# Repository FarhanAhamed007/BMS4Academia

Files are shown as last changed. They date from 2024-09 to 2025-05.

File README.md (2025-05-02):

# BMS4Academia



An educational Battery Management System (BMS) for academia: designed for students, research scholars, and hobbyist engaged in battery algorithm studies, enabling real-time testing of their algorithms and logics.

### Motive – To support research community with a habitat for testing of battery algorithms on battery packs

#### Developed for coherence and scalability 

### Key Features
-> Simple and community friendly Controller (ESP32S3)    
-> Master-Slave Architecture     
-> SPI and iso-SPI          
-> 3s to 100s configuration          
-> Cell balancing      
-> Contactor Control (12V/24V upto 3A) & Feedback      
-> CAN, RS485 and I2C Interface



I thank Rahul Marriesh for his contribution to 18s slave BMS development. 

I express my gratitude to Dr. Kaushal Jha, CEO of my center and co-guide, my guide Prof. Shankar Ram, and my mentor Dr. Sushant Mutagekar for their continuous support. I also extend my thanks to the **Center for Excellence in Energy and Telecommunication (CEET)** for providing the opportunity to develop this work. I am grateful to my ~~team~~ fam for their invaluable assistance and support throughout this project.

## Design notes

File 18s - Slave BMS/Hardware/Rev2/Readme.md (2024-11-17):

# 18s - Slave BMS      
## Design Language    
-> Simple design (2-Layer board)       
-> Easy to use       
-> Small in size (94mm x 90mm)

## Features     
-> Analog Devices AFE: LTC6813            
-> 0 - 5V voltage measurement of cells (NMC, LFP, LTO, Na-ion)        
-> Cell balancing up to 150mA per cell (External balancing)(balancing current can be increased by changing balancing resistors)       
-> SPI or Iso-SPI configurable          
-> Direct interface with any microcontroller (via SPI upto 18s)        
-> Configurable for temperature measurement via 10K thermistor or ADC for current measurement.     
-> 9x temperature sensing (thermistor based)         
                      (or)              
-> 8x temperature sensing (thermistor based) & 1x current sensing (AUX)       
-> Short circuit protection and wake-up interrupt by hardware design 

## PCB isometric


## PCB Sections & Connectors




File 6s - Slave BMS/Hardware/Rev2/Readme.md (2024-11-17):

# 6s - Slave BMS      
## Design Language   
-> Scalable (3 to 100s)      
-> Simple design (2-Layer board)           
-> dedicated current sensing port      
-> Small in size (51mm x 76mm)

## Features     
-> Analog Devices AFE: LTC6810         
-> 0 - 5V voltage measurement of cells (NMC, LFP, LTO, Na-ion, Zn-air etc...)        
-> Cell balancing up to 150mA per cell (internal balancing)       
-> SPI or Iso-SPI configurable          
-> External Power connector (Powering IC from external source instead of battery, useful for cells with low voltages like Zn-air)      
-> 3s to 100s           
-> Direct interface with any microcontroller (via SPI upto 6s)        
-> Configurable for temperature measurement via 10K thermistor or ADC for current measurement.     
-> 4x temperature sensing (thermistor based)         
                      (or)              
-> 3x temperature sensing (thermistor based) & 1x current sensing         

## PCB Sections & Connectors       
        



## PCB Configurations      


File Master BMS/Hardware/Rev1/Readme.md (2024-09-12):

# Master BMS      
## Design Language   
-> Multi-purpose (Use for Low voltage and High voltage systems)    
-> Simple design (2-Layer board)    
-> Ease of use, wide community support and powerful Microcontroller      
-> Isolation

## Features     
-> Powerful Microcontroller (ESP32S3)     
-> Compatible for Iso-SPI      
-> IOT capabilities      
-> Contactor based system    
-> 8x temperature sensing (thermistor based)     
-> 3x Contactor Control (Isolated)     
-> 2x Contactor Feedback (Isolated)     
-> 1x CAN (Isolated) and 1x RS485 (Isolated)     
-> 1x UART and 1x SLEEP      
-> 1x I2C and 1x SPI (either SPI or Iso-SPI)      
-> Arduino IDE compatible     
-> 1x Buzzer and 2x LED Indication (Programmable)

## PCB Sections



## PCB Connectors


## SPI/ISO-SPI Configurations


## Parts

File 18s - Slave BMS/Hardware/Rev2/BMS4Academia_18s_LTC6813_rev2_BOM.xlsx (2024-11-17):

Reference | Value | Footprint | Mouser/Online link | Qty
C1-C6, C14-C19, C26-C31, C42-C45 | C | Capacitor_SMD:C_0603_1608Metric |  | 22
C7-C13, C20-C25, C32-C37, C40, C41, C46 | 0.01uF | Capacitor_SMD:C_0603_1608Metric | https://www.mouser.in/ProductDetail/KYOCERA-AVX/KAE15AR72A103KT18 | 22
C38, C39, C47, C58 | 1uF | Capacitor_SMD:C_0603_1608Metric | https://www.mouser.in/ProductDetail/Samsung-Electro-Mechanics/CL10A105KA8NFNC?qs=%252B6g0mu59x7ItvV%2F7DV9Lig%3D%3D | 4
C48-C57 | 0.1uF | Capacitor_SMD:C_0603_1608Metric | https://www.mouser.in/ProductDetail/Samsung-Electro-Mechanics/CL10B104KA8WPNC?qs=i7qv8%2Fa7U0uUurI3oIH6aQ%3D%3D | 10
D1-D18 | GRN0603 | LED_SMD:LED_0603_1608Metric | https://www.mouser.in/ProductDetail/Wurth-Elektronik/150060RS75000?qs=LlUlMxKIyB3QnmZ3fw%2FVCA%3D%3D | 18
IC1 | LTC6813HLWE-1#3ZZPBF | LTC6813HLWE-1#3ZZPBF:QFP50P1200X1200X160-65N | https://www.mouser.in/ProductDetail/Analog-Devices/LTC6813HLWE-13ZZPBF?qs=lYGu3FyN48e3Qu9IYnRGuQ%3D%3D | 1
IC2, IC3 | TLV3202AIDR | TLV3202AIDR:SOIC127P600X175-8N | https://www.mouser.in/ProductDetail/Texas-Instruments/TLV3202AIDR?qs=b5Ofe9I6AaEmC9QJ6LA68w%3D%3D | 2
J1 | Conn_01x19_Socket | Connector_PinSocket_2.54mm:PinSocket_1x19_P2.54mm_Horizontal | Local | 1
J2 | SPI connector | Connector_Molex:Molex_PicoBlade_53048-0410_1x04_P1.25mm_Horizontal | Local | 1
J3 | iso SPI B | Connector_JST:JST_PH_S2B-PH-K_1x02_P2.00mm_Horizontal | https://robu.in/product/s2b-ph-klfsn-jst-1x2p-2p-ph-tin-2-25%E2%84%8385%E2%84%83-2a-1-2mm-brass-bend-insert-push-pullp2mm-wire-to-board-connector-rohs/?gad_so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 | 1
J4 | iso SPI A | Connector_JST:JST_PH_S2B-PH-K_1x02_P2.00mm_Horizontal | https://robu.in/product/s2b-ph-klfsn-jst-1x2p-2p-ph-tin-2-25%E2%84%8385%E2%84%83-2a-1-2mm-brass-bend-insert-push-pullp2mm-wire-to-board-connector-rohs/?gad_so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 | 1
J5 | Conn_01x16_Socket | Connector_PinSocket_2.00mm:PinSocket_2x08_P2.00mm_Vertical | Local | 1
J6 | AUX connector | Connector_JST:JST_PH_S2B-PH-K_1x02_P2.00mm_Horizontal | https://robu.in/product/s2b-ph-klfsn-jst-1x2p-2p-ph-tin-2-25%E2%84%8385%E2%84%83-2a-1-2mm-brass-bend-insert-push-pullp2mm-wire-to-board-connector-rohs/?gad_so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 | 1
J7 | Conn_01x04_Pin | Connector_JST:JST_PH_S4B-PH-K_1x04_P2.00mm_Horizontal | https://robu.in/product/s4b-ph-kllfsn-jst-1x4p-4p-ph-tin-4-25%e2%84%8385%e2%84%83-2a-1-2mm-copper-alloy-bend-insert-push-pullp2mm-wire-to-board-connector-rohs/ | 1
Q1-Q18 | BSS308PEH6327XTSA1 | LIB_BSS308PEH6327XTSA1:PG-SOT-23 | https://www.mouser.in/ProductDetail/Infineon-Technologies/BSS308PEH6327XTSA1?qs=K00xGehIljswKa%252BUULwt9w%3D%3D&gad_source=1 | 18
Q19 | DXT5551P5 -13 | LIB_DXT5551P5-13:DXT5551P513 | https://www.mouser.in/ProductDetail/Diodes-Incorporated/DXT5551P5-13?qs=pmB%252BthhaMeURGx362MbdPw%3D%3D | 1
R1-R6, R26-R31, R50-R55 | 220R | Resistor_SMD:R_0603_1608Metric | https://www.mouser.in/ProductDetail/Panasonic/ERJ-3GEYJ221V?qs=4WZYzuGhm5qHCFSN9go8VQ%3D%3D | 18
R7-R12, R32-R37, R56-R61 | 33R | Resistor_SMD:R_2512_6332Metric_Pad1.40x3.35mm_HandSolder | https://www.mouser.in/ProductDetail/Panasonic/ERJ-U03J330V?qs=pdFhdcvjjggQnG%2Fkef10pA%3D%3D | 18
R13-R19, R38-R43, R62-R67, R80, R83 | 100R | Resistor_SMD:R_0603_1608Metric | https://www.mouser.in/ProductDetail/Kamaya/RMC1-16K101FTP | 21
R20-R25, R44-R49, R68-R73 | 3K3 | Resistor_SMD:R_0603_1608Metric | https://www.mouser.in/ProductDetail/Panasonic/ERJ-3GEYJ332V | 18
R74, R75, R85-R92, R99 | 1K | Resistor_SMD:R_0603_1608Metric | https://www.mouser.in/ProductDetail/KOA-Speer/RK73B1JTTD102J?qs=sGAEpiMZZMvdGkrng054t5lOknjIQAOXgZiho2sE8bc%3D | 11
R76-R79 | 49.9R | Resistor_SMD:R_0603_1608Metric | https://www.mouser.in/ProductDetail/KOA-Speer/RK73H1JTTD49R9F?qs=sGAEpiMZZMvdGkrng054tzl5geC4ftCSdzgtDUUUvgk%3D | 4
R81, R82, R84, R97 | 1M | Resistor_SMD:R_0603_1608Metric | https://www.mouser.in/ProductDetail/Kamaya/RMC1-16K1004FTP | 4
R93-R96, R98, R100-R103, R114-R116 | 10K | Resistor_SMD:R_0603_1608Metric | https://www.mouser.in/ProductDetail/Panasonic/ERJ-3GEYJ103V | 12
R104, R110 | 0R | Resistor_SMD:R_0603_1608Metric_Pad0.98x0.95mm_HandSolder | https://www.mouser.in/ProductDetail/Vishay-Dale/RCC06030000Z0EA?qs=GedFDFLaBXGafTcDIEa6hQ%3D%3D | 2
R105, R107 | 100K | Resistor_SMD:R_0603_1608Metric | https://www.mouser.in/ProductDetail/Vishay-Dale/CRCW0603100KFKEAHP | 2
R106 | 825K | Resistor_SMD:R_0603_1608Metric | https://www.mouser.in/ProductDetail/YAGEO/RC0603FR-07825KL?qs=sGAEpiMZZMvdGkrng054tzHTiABLtXX4S3I6ECsileU%3D | 1
R108 | 8K | Resistor_SMD:R_0603_1608Metric | https://www.mouser.in/ProductDetail/Vishay-Dale/CRCW06038K06FKEAHP | 1
R109, R112 | 8M25 | Resistor_SMD:R_0603_1608Metric | https://www.mouser.in/ProductDetail/Vishay-Dale/CRCW06038M25FKEA?qs=sGAEpiMZZMvdGkrng054t9YoKDts9whpxxNmV7MOV1U%3D | 2
R111 | 604K | Resistor_SMD:R_0603_1608Metric | https://www.mouser.in/ProductDetail/Panasonic/ERJ-3EKF6043V | 1
R113 | 2M74 | Resistor_SMD:R_0603_1608Metric | https://www.mouser.in/ProductDetail/Vishay-Dale/CRCW06032M74FKEA | 1
R117 | 9k76 | Resistor_SMD:R_0603_1608Metric | https://www.mouser.in/ProductDetail/Panasonic/ERJ-3EKF9761?qs=sGAEpiMZZMvdGkrng054t17fN4yPK5c4yewBHkIurQ8%3D | 1
T1 | HM2100NL | HM2100NL:SOP254P1493X345-10N | https://www.mouser.co.uk/ProductDetail/Pulse-Electronics/HM2100NL?qs=1mbolxNpo8dwDSBbBgCdLQ%3D%3D | 1
U1, U2 | SN74AHC1G08DBVR | SN74AHC1G08DBVR:SOT95P280X145-5N | https://www.mouser.in/ProductDetail/Texas-Instruments/SN74AHC1G08DBVR?qs=tJ5HNKWh3OXzGHgsEkuHbw%3D%3D | 2

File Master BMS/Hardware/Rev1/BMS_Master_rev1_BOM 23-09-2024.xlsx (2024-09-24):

S.No | Reference | Value | Footprint | Datasheet | Qty
1 | C1-C4 | 0.01uF | Capacitor_SMD:C_0603_1608Metric_Pad1.08x0.95mm_HandSolder | https://www.mouser.in/ProductDetail/Murata-Electronics/GCM188R72A103KA37J?qs=XuOgWozpmAS9MToLIJ09hw%3D%3D | 4
2 | C5, C6, C9, C14, C16, C22, C26, C32, C35, C42 | 0.1uF | Capacitor_SMD:C_0603_1608Metric_Pad1.08x0.95mm_HandSolder | https://www.mouser.in/ProductDetail/Samsung-Electro-Mechanics/CL10B104KA85PNC?qs=xZ%2FP%252Ba9zWqabsWCtlKJ0Xw%3D%3D | 10
3 | C7, C10, C21, C25, C31, C34 | 1uF | Capacitor_SMD:C_0603_1608Metric_Pad1.08x0.95mm_HandSolder | https://www.mouser.in/ProductDetail/TDK/CGA3E1X5R1C105K080AC?qs=xLDY6iXSiQY64eaD0ZTXHg%3D%3D | 6
4 | C8, C20, C24, C27, C33 | 10uF | Capacitor_SMD:C_0603_1608Metric_Pad1.08x0.95mm_HandSolder | https://www.mouser.in/ProductDetail/Murata-Electronics/GRM188R61E106KA73J?qs=5aG0NVq1C4xEV8YyiSS7mg%3D%3D | 5
5 | C11 | EEE-1VA101XP | EEE-1VA101XP:EEE0JA331XP | https://www.mouser.in/ProductDetail/Panasonic/EEE-1VA101XP?qs=wEytwf7f49FM0EqQXrBRGQ%3D%3D | 1
6 | C12 | EEE-1CA100SR | EEE-1CA100SR:EEE1AA220WR | https://www.mouser.in/ProductDetail/Panasonic/EEE-1CA100SR?qs=ANJC8C65Mw5HUsKv8znGCA%3D%3D | 1
7 | C13, C15 | 10uF | Capacitor_SMD:C_0805_2012Metric_Pad1.18x1.45mm_HandSolder | https://www.mouser.in/ProductDetail/Samsung-Electro-Mechanics/CL21A106KOQNNNG?qs=hqM3L16%252BxlcMWI7QbqH0LA%3D%3D | 2
8 | C17, C18, C28-C30, C36-C38 | 0.1uF | Capacitor_SMD:C_0603_1608Metric | https://www.mouser.in/ProductDetail/Samsung-Electro-Mechanics/CL10B104KA85PNC?qs=xZ%2FP%252Ba9zWqabsWCtlKJ0Xw%3D%3D | 8
9 | C19, C23 | 100pF | Capacitor_SMD:C_0603_1608Metric_Pad1.08x0.95mm_HandSolder | https://www.mouser.in/ProductDetail/Wurth-Elektronik/885012006038?qs=0KOYDY2FL288CAvsydBFIA%3D%3D | 2
10 | C39 | 4700pF | Capacitor_SMD:C_0603_1608Metric_Pad1.08x0.95mm_HandSolder | https://www.mouser.in/ProductDetail/Wurth-Elektronik/885012206063?qs=0KOYDY2FL285eK3hQulgUw%3D%3D | 1
11 | C40, C41 | 68pF | Capacitor_SMD:C_0603_1608Metric_Pad1.08x0.95mm_HandSolder | https://www.mouser.in/ProductDetail/Wurth-Elektronik/885012006037?qs=0KOYDY2FL29wQtLEeocm%2Fg%3D%3D | 2
12 | D1-D3 | LED | LED_SMD:LED_0603_1608Metric_Pad1.05x0.95mm_HandSolder | https://www.mouser.in/ProductDetail/710-150060RS75000 | 3
13 | D4 | 1N4148 | Diode_SMD:D_SOD-323 | https://www.mouser.in/ProductDetail/Diodes-Incorporated/1N4148WS-7-F?qs=4drIV0IxA0r8aNy7%2Fu4kVw%3D%3D | 1
14 | D5-D7 | 1N4001 | Diode_THT:D_DO-41_SOD81_P10.16mm_Horizontal | https://www.mouser.in/ProductDetail/Diotec-Semiconductor/1N4001S?qs=OlC7AqGiEDlz7DNH7DR%252BLA%3D%3D | 3
15 | D8, D9 | SM712_SOT23 | Package_TO_SOT_SMD:SOT-23 | https://www.mouser.in/ProductDetail/Micro-Commercial-Components-MCC/SM712-TP?qs=WJd%252B7yD6my3J3yaz9R6ciw%3D%3D | 2
16 | IC1 | LTC6820IMS#TRPBF | LTC6820IMS:SOP50P490X110-16N | https://www.mouser.in/ProductDetail/Analog-Devices/LTC6820IMSTRPBF?qs=hVkxg5c3xu8J%252BEL4cIWawA%3D%3D | 1
17 | IC2 | ESP32-S3-WROOM-1-N8R2 | ESP32-S3-WROOM1-N8R2:ESP32S3WROOM1N8R2 | https://www.mouser.in/ProductDetail/Espressif-Systems/ESP32-S3-WROOM-1U-N8R2 | 1
18 | J1-J6, J9, J13-J15 | Conn_01x02_Socket | Connector_JST:JST_XH_B2B-XH-A_1x02_P2.50mm_Vertical | User specific | 10
19 | J8 | USB_B_Mini | Connector_USB:USB_Mini-B_Wuerth_65100516121_Horizontal | https://www.mouser.in/ProductDetail/Wurth-Elektronik/65100516121?qs=rS3zZhy2AQPLyCguT204Og%3D%3D | 1
20 | J10 | Conn_01x02_Socket | Connector_PinHeader_1.27mm:PinHeader_1x02_P1.27mm_Vertical | User specific | 1
21 | J11 | Conn_01x02_Socket | Connector_Molex:Molex_PicoBlade_53047-0210_1x02_P1.25mm_Vertical | User specific | 1
22 | J12 | Conn_01x04_Socket | Connector_PinSocket_1.27mm:PinSocket_1x04_P1.27mm_Vertical | User specific | 1
23 | J16, J17 | Screw_Terminal_01x02 | Connector_JST:JST_XH_B2B-XH-A_1x02_P2.50mm_Vertical | User specific | 2
24 | J18 | Conn_01x16_Socket | Connector_PinSocket_2.00mm:PinSocket_2x08_P2.00mm_Vertical | User specific | 1
25 | J19 | Conn_01x04_Socket | Connector_JST:JST_XH_B4B-XH-A_1x04_P2.50mm_Vertical | User specific | 1
26 | JP1 | Jumper_2_Open | Resistor_SMD:R_1210_3225Metric | https://www.mouser.in/ProductDetail/SEI-Stackpole/RMCF1210ZT0R00?qs=IPgv5n7u5Qab9%2FkbHEqwzw%3D%3D | 1
27 | L1, L2 | 51uH 0.2A 1R | TDK_common_mode_choke:IND_ACT45R_TDK | https://www.mouser.in/ProductDetail/810-ACT45B5102PTL003 | 2
28 | LS1 | AI-1223-TWT-5V-R | AI-1223-TWT-5V-R:AI1223TWT5VR | https://www.mouser.in/ProductDetail/PUI-Audio/AI-1223-TWT-5V-5-R?qs=vJF2aRtctcCUdTWcaVGelg%3D%3D | 1
29 | Q1 | DMN2310U-7 | DMN2310U-7:SOT96P240X110-3N | https://www.mouser.in/ProductDetail/621-DMN2310U-7 | 1
30 | Q2-Q4 | PSMN017-60YS,115 | Package_TO_SOT_SMD:LFPAK56 | https://www.mouser.in/ProductDetail/Nexperia/PSMN017-60YS115?qs=O%2F7ihdSJpeaj9vl3Dyu0og%3D%3D | 3
31 | Q5, Q6 | S8050 | MMS8050-H-TP:SOT95P237X125-3N | https://www.mouser.in/ProductDetail/Micro-Commercial-Components-MCC/MMS8050-H-TP?qs=y6ZabgHbY%252Bwohxnqwm2Wtw%3D%3D | 2
32 | R1, R5, R6 | 470R | Resistor_SMD:R_0603_1608Metric_Pad0.98x0.95mm_HandSolder | https://www.mouser.in/ProductDetail/Panasonic/ERJ-PA3F4750V?qs=BzJM0faLVqWOPTWURmls9Q%3D%3D | 3
33 | R2-R4, R7-R10 | 220R | Resistor_SMD:R_0603_1608Metric_Pad0.98x0.95mm_HandSolder | https://www.mouser.in/ProductDetail/Panasonic/ERJ-PA3F2200V?qs=BzJM0faLVqXVFpMbvWqlzQ%3D%3D | 7
34 | R11-R14, R34-R36, R38, R60, R61, R72 | 10K | Resistor_SMD:R_0603_1608Metric_Pad0.98x0.95mm_HandSolder | https://www.mouser.in/ProductDetail/Panasonic/ERJ-PA3F1002V?qs=BzJM0faLVqWQDmJ9zpwcmw%3D%3D | 11
35 | R15, R17, R26, R27, R30, R31 | 1K | Resistor_SMD:R_0603_1608Metric_Pad0.98x0.95mm_HandSolder | https://www.mouser.in/ProductDetail/Vishay-Dale/RCS060349R9FKEA | 6
36 | R16, R18 | 2K | Resistor_SMD:R_0603_1608Metric_Pad0.98x0.95mm_HandSolder | https://www.mouser.in/ProductDetail/Vishay-Dale/CRCW06032K00FKEAHP?qs=k2%2FDWSARqgE7PHJQlU2Sxw%3D%3D | 2
37 | R19-R25, R32, R33, R37, R39-R43, R48, R49, R53, R54, R58, R59, R75, R76 | 0R | Resistor_SMD:R_0603_1608Metric_Pad0.98x0.95mm_HandSolder | https://www.mouser.in/ProductDetail/Vishay-Dale/RCC06030000Z0EA?qs=GedFDFLaBXGafTcDIEa6hQ%3D%3D | 23
38 | R28, R29 | 60.1 | Resistor_SMD:R_0603_1608Metric_Pad0.98x0.95mm_HandSolder | https://www.mouser.in/ProductDetail/Panasonic/ERJ-PA3F60R4V?qs=BzJM0faLVqVCXA%252Bk%2FOWiUA%3D%3D | 2
39 | R44, R45, R50-R52, R65-R67 | 1K | Resistor_SMD:R_0603_1608Metric | https://www.mouser.in/ProductDetail/Vishay-Dale/RCS060349R9FKEA | 8
40 | R46, R47, R55-R57, R68-R70 | 10K | Resistor_SMD:R_0603_1608Metric | https://www.mouser.in/ProductDetail/Panasonic/ERJ-PA3F1002V?qs=BzJM0faLVqWQDmJ9zpwcmw%3D%3D | 8
41 | R62, R71 | 120R | Resistor_SMD:R_0603_1608Metric_Pad0.98x0.95mm_HandSolder | https://www.mouser.in/ProductDetail/KOA-Speer/SG73P1JTTD1200F?qs=mxuPqPjQq7Hkr7xDKFt6dw%3D%3D | 2
42 | R63, R64 | 59R | Resistor_SMD:R_0603_1608Metric_Pad0.98x0.95mm_HandSolder | https://www.mouser.in/ProductDetail/Vishay-Dale/RCS060359R0FKEA?qs=AAB0DUhlpks%252B68nNzXHOnw%3D%3D | 2
43 | R73, R74 | 4K7 | Resistor_SMD:R_0603_1608Metric | https://www.mouser.in/ProductDetail/Panasonic/ERJ-PA3F4701V?qs=BzJM0faLVqXqRP4bd2SzhQ%3D%3D | 2
44 | SW1 | RST | Button_Switch_SMD:SW_Push_1P1T_NO_6x6mm_H9.5mm | https://www.mouser.in/ProductDetail/CUI-Devices/TS04-66-43-BK-160-SMT?qs=A6eO%252BMLsxmRO%252BN2ogoDtCQ%3D%3D | 1
45 | SW2 | BOOT0 | Button_Switch_SMD:SW_Push_1P1T_NO_6x6mm_H9.5mm | https://www.mouser.in/ProductDetail/CUI-Devices/TS04-66-43-BK-160-SMT?qs=A6eO%252BMLsxmRO%252BN2ogoDtCQ%3D%3D | 1
46 | T1 | HM2101NL | HM2101NL:HM2101NL | https://www.mouser.in/ProductDetail/Pulse-Electronics/HM2101NL?qs=1mbolxNpo8erPUsgpz%252BJAA%3D%3D | 1
47 | U1-U5 | PC817 | Package_DIP:DIP-4_W7.62mm | https://www.mouser.in/ProductDetail/Sharp-Microelectronics/PC817X2NSZ9F?qs=rrS6PyfT74ehABo1g8zXHw%3D%3D | 5
48 | U6 | USBLC6-2P6 | Package_TO_SOT_SMD:SOT-666 | https://www.mouser.in/ProductDetail/STMicroelectronics/USBLC6-2P6?qs=6ARB0lp6jlViGcbUSvj1Mw%3D%3D | 1
49 | U7 | CH340G | Package_SO:SOIC-16_3.9x9.9mm_P1.27mm | https://robu.in/product/ch340g-soic16-usb-to-serial-ttl-rs232-converter-ic/ | 1
50 | U8 | VRA_ZP-6WR3 | VRB_ZP-6WR3:VRB_ZP-6WR3 | https://www.amarradio.com/sku/ITM23621 | 1
51 | U9 | AMS1117-5.0 | Package_TO_SOT_SMD:SOT-223-3_TabPin2 | https://www.mouser.in/ProductDetail/onsemi/LM1117MPX-50NOPB?qs=DPoM0jnrROW5saxbk%2FgBxA%3D%3D | 1
52 | U10 | ISO1042DWV | Package_SO:SOIC-8_7.5x5.85mm_P1.27mm | https://www.mouser.in/ProductDetail/Texas-Instruments/ISO1042BDWVR?qs=qSfuJ%252Bfl%2Fd68DAhWt0GTEQ%3D%3D | 1
53 | U11 | ISO3082DW | Package_SO:SOIC-16W_7.5x10.3mm_P1.27mm | https://www.mouser.in/ProductDetail/Texas-Instruments/ISO3082DW?qs=5gBG3L055oOba23GzaXsQQ%3D%3D | 1
54 | U13 | NCD9830DBR2G | NCD9830DBR2G_2:IC_MC14040BDTR2G | https://www.mouser.in/ProductDetail/onsemi/NCD9830DBR2G?qs=xGcJQ%252BnsJwuRbKLXZSG0bw%3D%3D | 1

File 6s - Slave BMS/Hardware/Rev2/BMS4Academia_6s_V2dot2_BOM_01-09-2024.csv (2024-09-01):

S.No | Reference | Value | Footprint | Mouser | Qty
1 | C1-C8, C12, C13, C17-C20 | 10nF | Capacitor_SMD:C_0603_1608Metric | https://www.mouser.in/ProductDetail/Murata-Electronics/GCM188R72A103KA37J?qs=XuOgWozpmAS9MToLIJ09hw%3D%3D | 14
2 | C9-C11 | 1uF | Capacitor_SMD:C_0603_1608Metric | https://www.mouser.in/ProductDetail/TDK/CGA3E1X5R1C105K080AC?qs=xLDY6iXSiQY64eaD0ZTXHg%3D%3D | 3
3 | C14-C16, C21 | 0.1uF | Capacitor_SMD:C_0603_1608Metric | https://www.mouser.in/ProductDetail/Samsung-Electro-Mechanics/CL10B104KA85PNC?qs=xZ%2FP%252Ba9zWqabsWCtlKJ0Xw%3D%3D | 4
4 | D1-D7 | LED | LED_SMD:LED_0603_1608Metric | https://www.mouser.in/ProductDetail/Wurth-Elektronik/150060RS75000?qs=LlUlMxKIyB3QnmZ3fw%2FVCA%3D%3D | 7
5 | D8-D13 | MBR0520 | Diode_SMD:D_SOD-123 | https://www.mouser.in/ProductDetail/Micro-Commercial-Components-MCC/MBR0520L-TP?qs=J4%252BvTxtW289z%2FynXXxISdw%3D%3D | 6
6 | J1 | Voltage harness | Connector_JST:JST_XH_S7B-XH-A-1_1x07_P2.50mm_Horizontal | https://www.digikey.in/en/products/detail/jst-sales-america-inc/S7B-XH-A/1651038 | 1
7 | J2, J5, J6 | Conn_01x02_Socket | Connector_JST:JST_XH_S2B-XH-A-1_1x02_P2.50mm_Horizontal | https://www.digikey.in/en/products/detail/jst-sales-america-inc/S2B-XH-A-1/9961922 | 3
8 | J3 | Conn_01x04_Socket | Connector_Molex:Molex_PicoBlade_53048-0410_1x04_P1.25mm_Horizontal | https://www.mouser.in/ProductDetail/Molex/53048-0410?qs=359VwiUTsp2msj5Tobchuw%3D%3D | 1
9 | J4 | Conn_01x08_Socket | 61200821721:61200821721 | https://www.mouser.in/ProductDetail/Wurth-Elektronik/61200821721?qs=PhR8RmCirEb56BXUsQNR%2FQ%3D%3D | 1
10 | Q1 | FCX491QTA | Package_TO_SOT_SMD:SOT-89-3 | https://www.mouser.in/ProductDetail/Diodes-Incorporated/FCX491QTA?qs=u16ybLDytRbbtrTmReU6XA%3D%3D | 1
11 | R1, R9, R39 | 0R | Resistor_SMD:R_0603_1608Metric_Pad0.98x0.95mm_HandSolder | https://www.mouser.in/ProductDetail/Vishay-Dale/RCC06030000Z0EA?qs=GedFDFLaBXGafTcDIEa6hQ%3D%3D | 3
12 | R2-R8 | 220R | Resistor_SMD:R_0603_1608Metric | https://www.mouser.in/ProductDetail/Panasonic/ERJ-PA3F2200V?qs=BzJM0faLVqXVFpMbvWqlzQ%3D%3D | 7
13 | R10-R16 | 15R 2512 | Resistor_SMD:R_2512_6332Metric | https://www.mouser.in/ProductDetail/Bourns/CR2512-FX-15R0ELF?qs=LzTMQcCtZ7sBeA1dGxVDgQ%3D%3D | 7
14 | R17-R24 | 100R 1% | Resistor_SMD:R_0603_1608Metric | https://www.mouser.in/ProductDetail/Panasonic/ERJ-PA3F1000V?qs=sGAEpiMZZMtlubZbdhIBIL24R7XL4VFWuWjJwK1uHL8%3D | 8
15 | R25, R26, R31-R33, R37 | 1K | Resistor_SMD:R_0603_1608Metric | https://www.mouser.in/ProductDetail/Vishay-Dale/RCS060349R9FKEA | 2
16 | R27-R30 | 49.9R | Resistor_SMD:R_0603_1608Metric | https://www.mouser.in/ProductDetail/Panasonic/ERJ-PA3F1001V?qs=sGAEpiMZZMtlubZbdhIBIEk08ppm7bLPCsocysv3bJ4%3D | 4
17 | R34-R36, R38 | 10K | Resistor_SMD:R_0603_1608Metric | https://www.mouser.in/ProductDetail/Panasonic/ERJ-PA3F1002V?qs=BzJM0faLVqWQDmJ9zpwcmw%3D%3D | 4
18 | T1 | HM2100NL | HM2100NL:SOP254P1493X345-10N | https://www.mouser.in/ProductDetail/Pulse-Electronics/HM2100NLT?qs=lYGu3FyN48d%2FM7DDmrViPA%3D%3D | 1
19 | U1 | LTC6810HG-1-3ZZPBF | LTC6810:05-08-1754_ADI | https://www.mouser.in/ProductDetail/Analog-Devices/LTC6810HG-13ZZPBF?qs=byeeYqUIh0PWO%252B24TZQ4ZA%3D%3D | 1

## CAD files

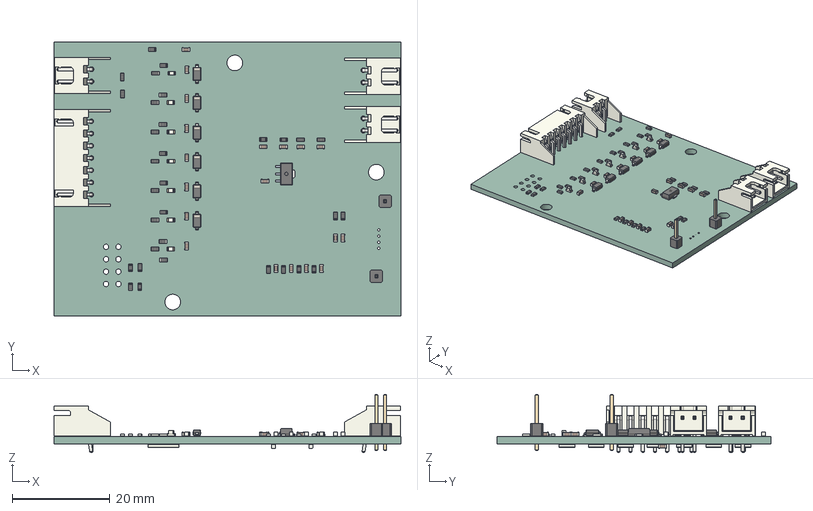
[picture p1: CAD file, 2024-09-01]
6s - Slave BMS/Hardware/Rev2/BMS4Academia_6s_v2dot2_CAD.step
71.0 x 56.0 x 11.9 mm
LTC6810_base1 PCB

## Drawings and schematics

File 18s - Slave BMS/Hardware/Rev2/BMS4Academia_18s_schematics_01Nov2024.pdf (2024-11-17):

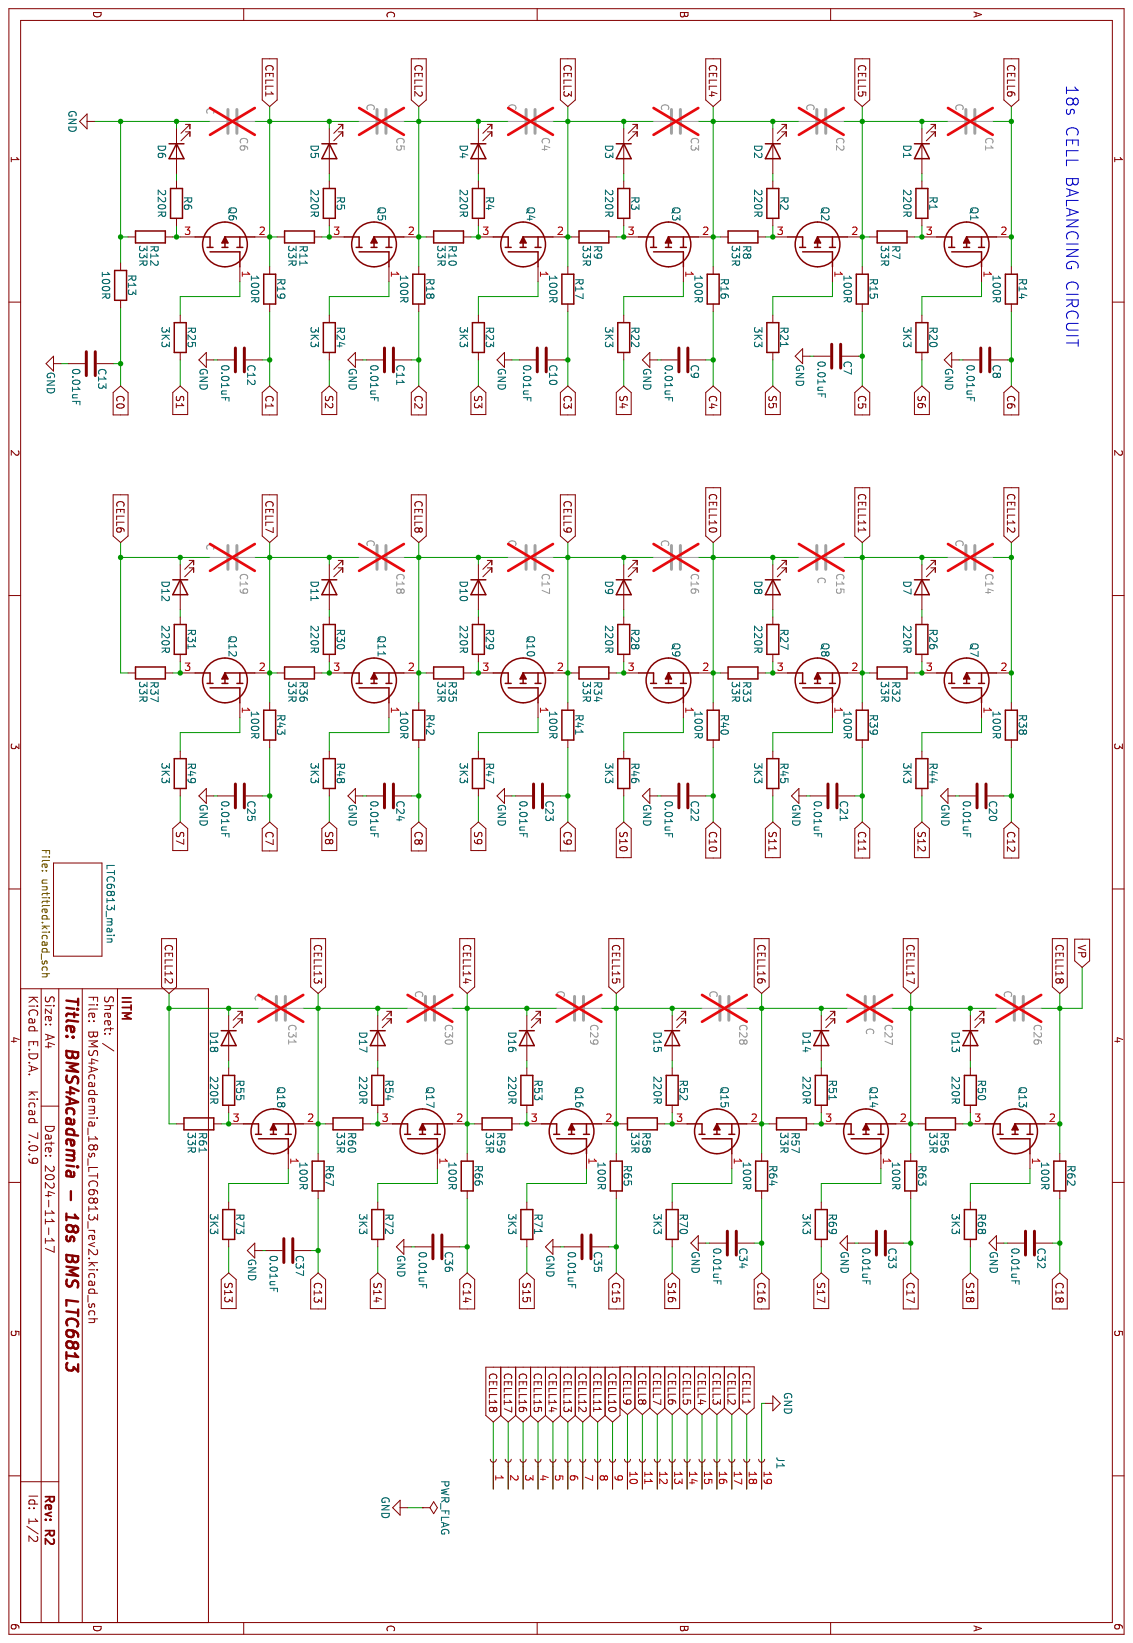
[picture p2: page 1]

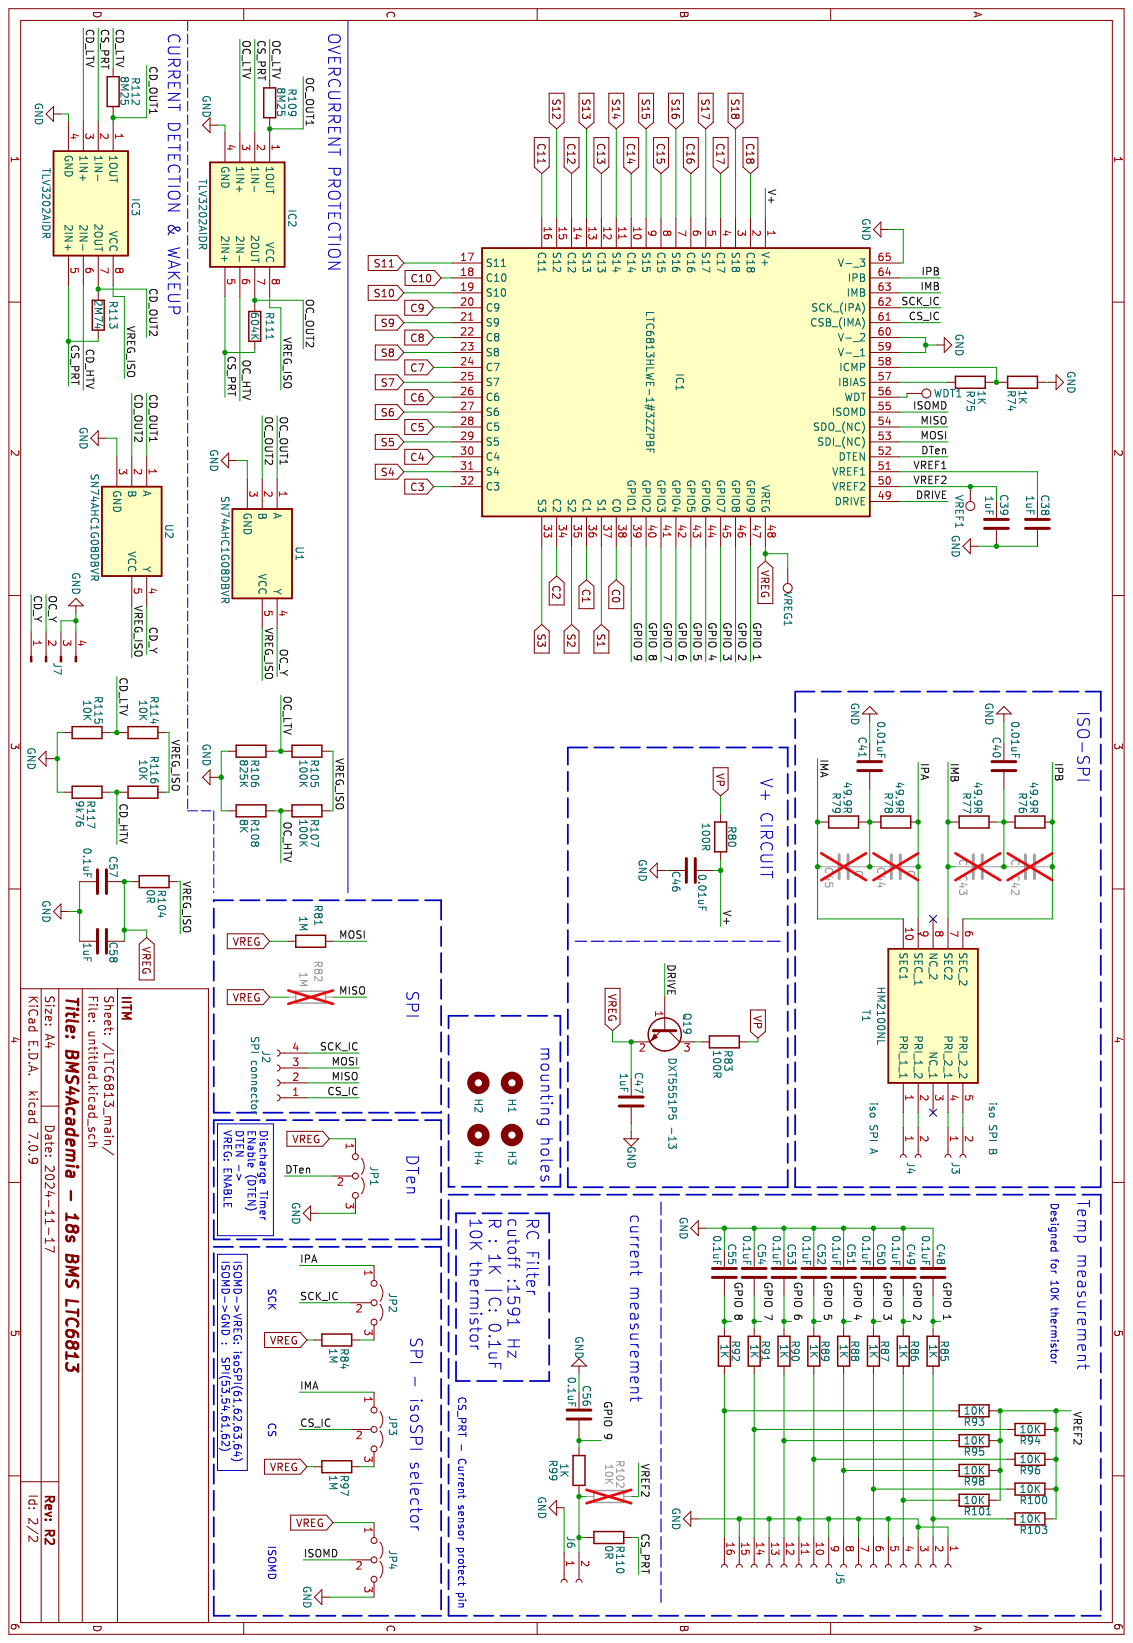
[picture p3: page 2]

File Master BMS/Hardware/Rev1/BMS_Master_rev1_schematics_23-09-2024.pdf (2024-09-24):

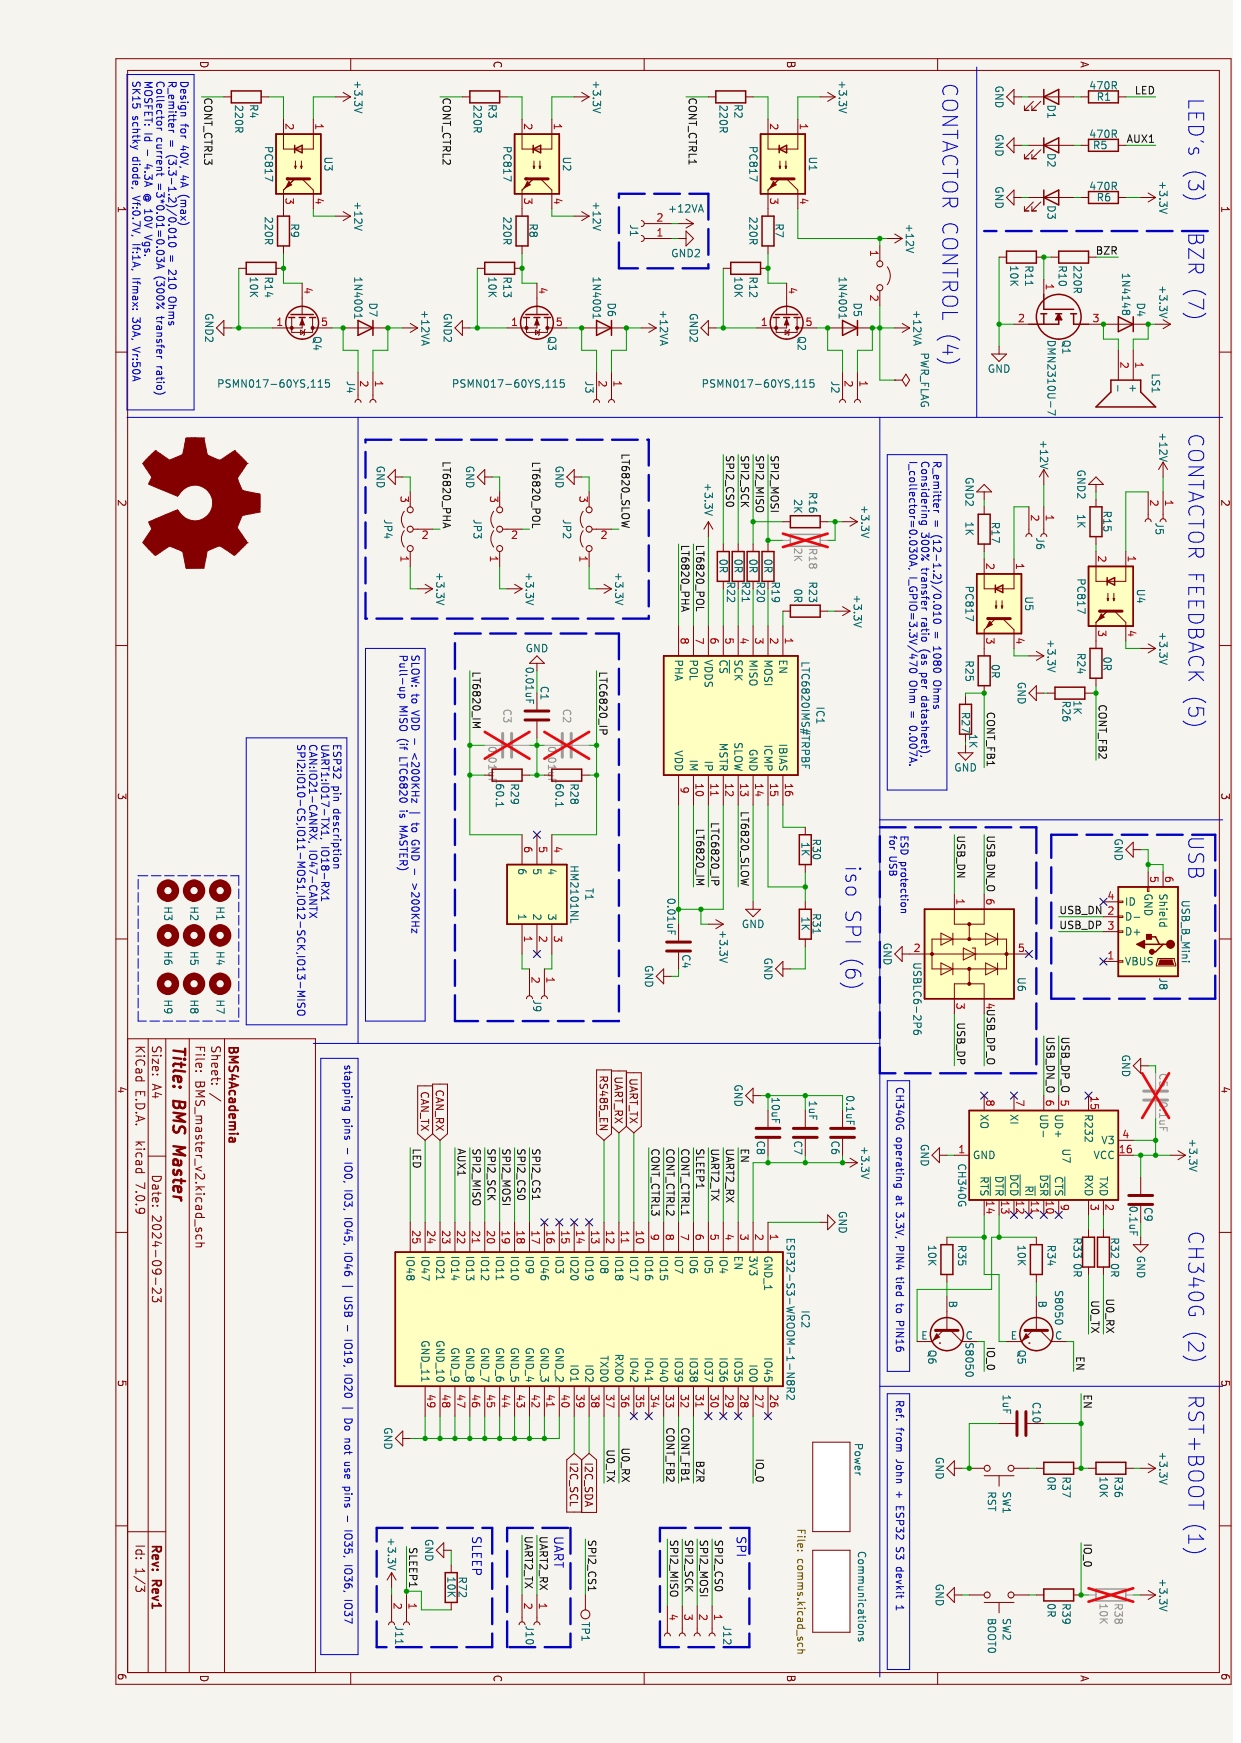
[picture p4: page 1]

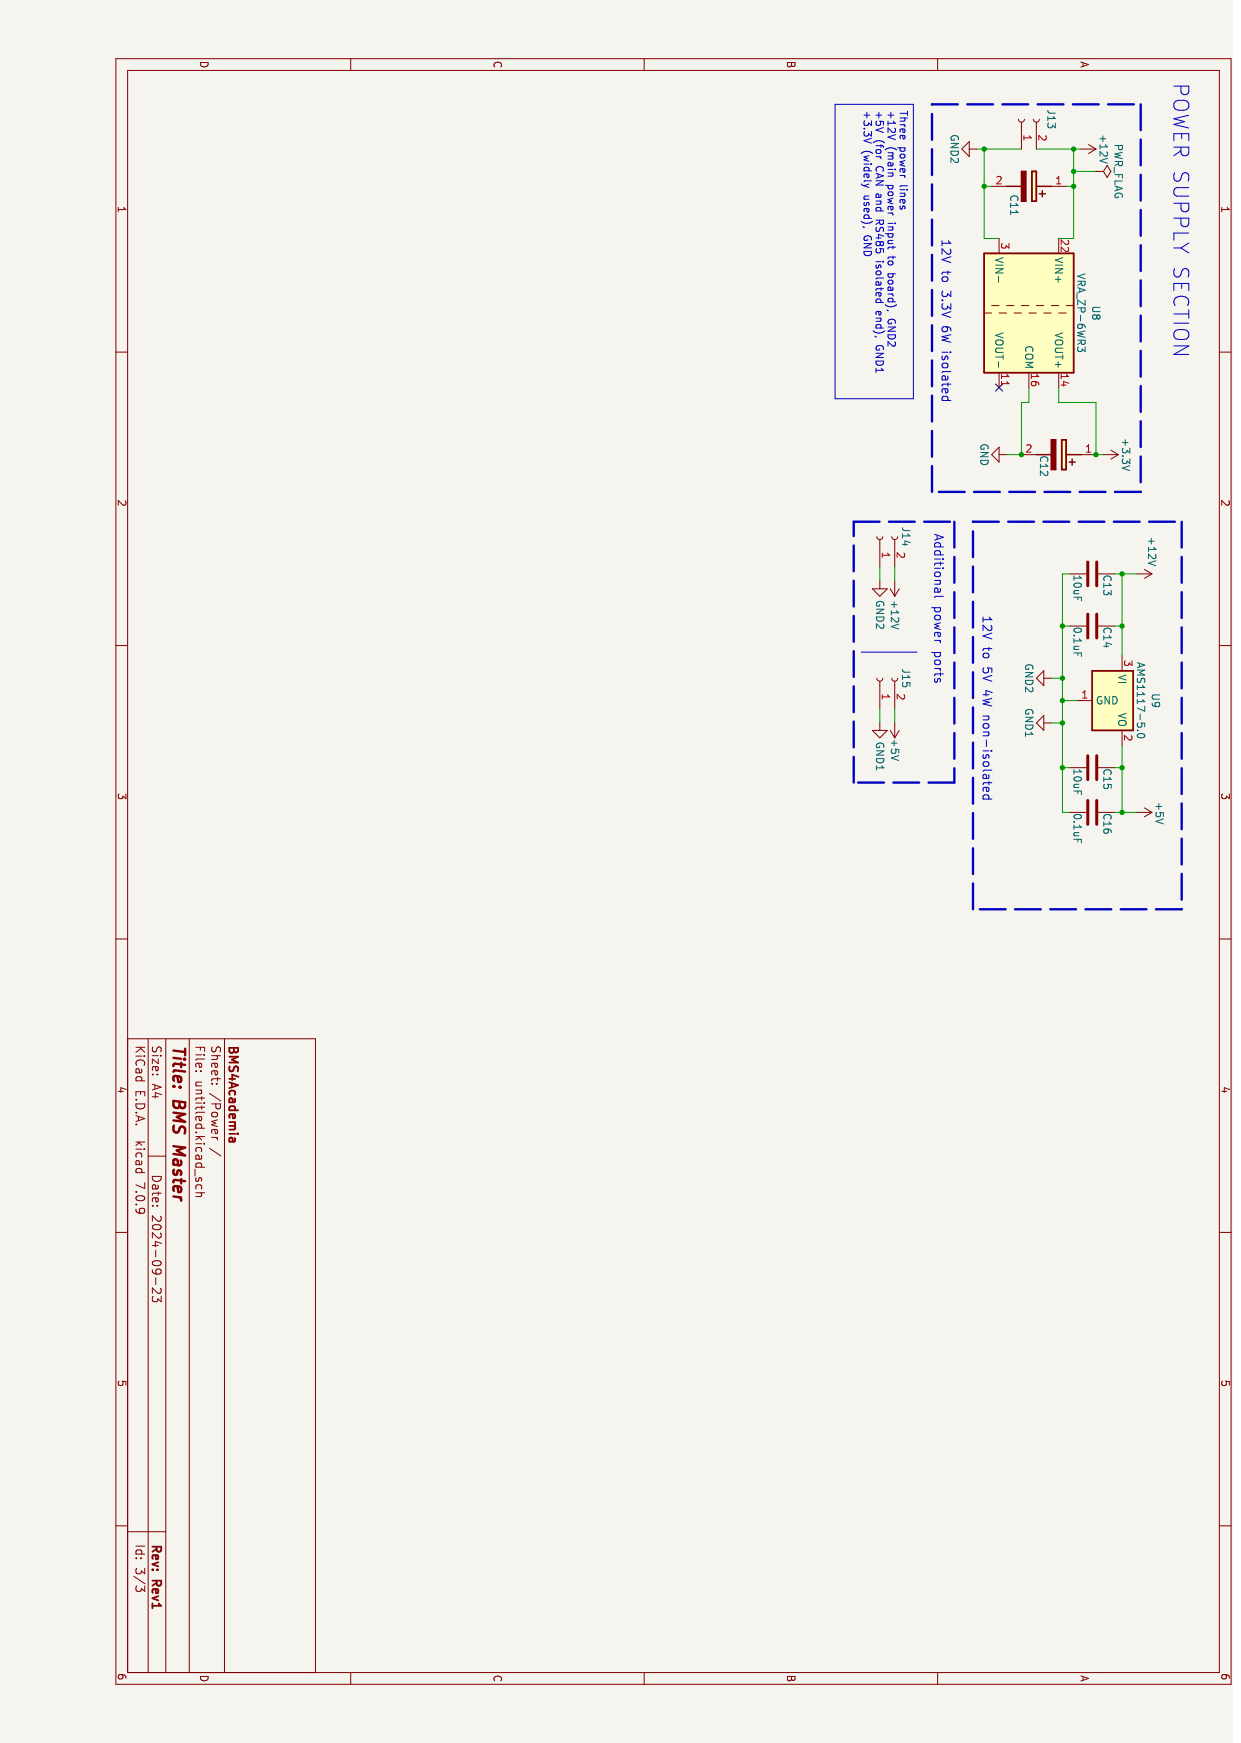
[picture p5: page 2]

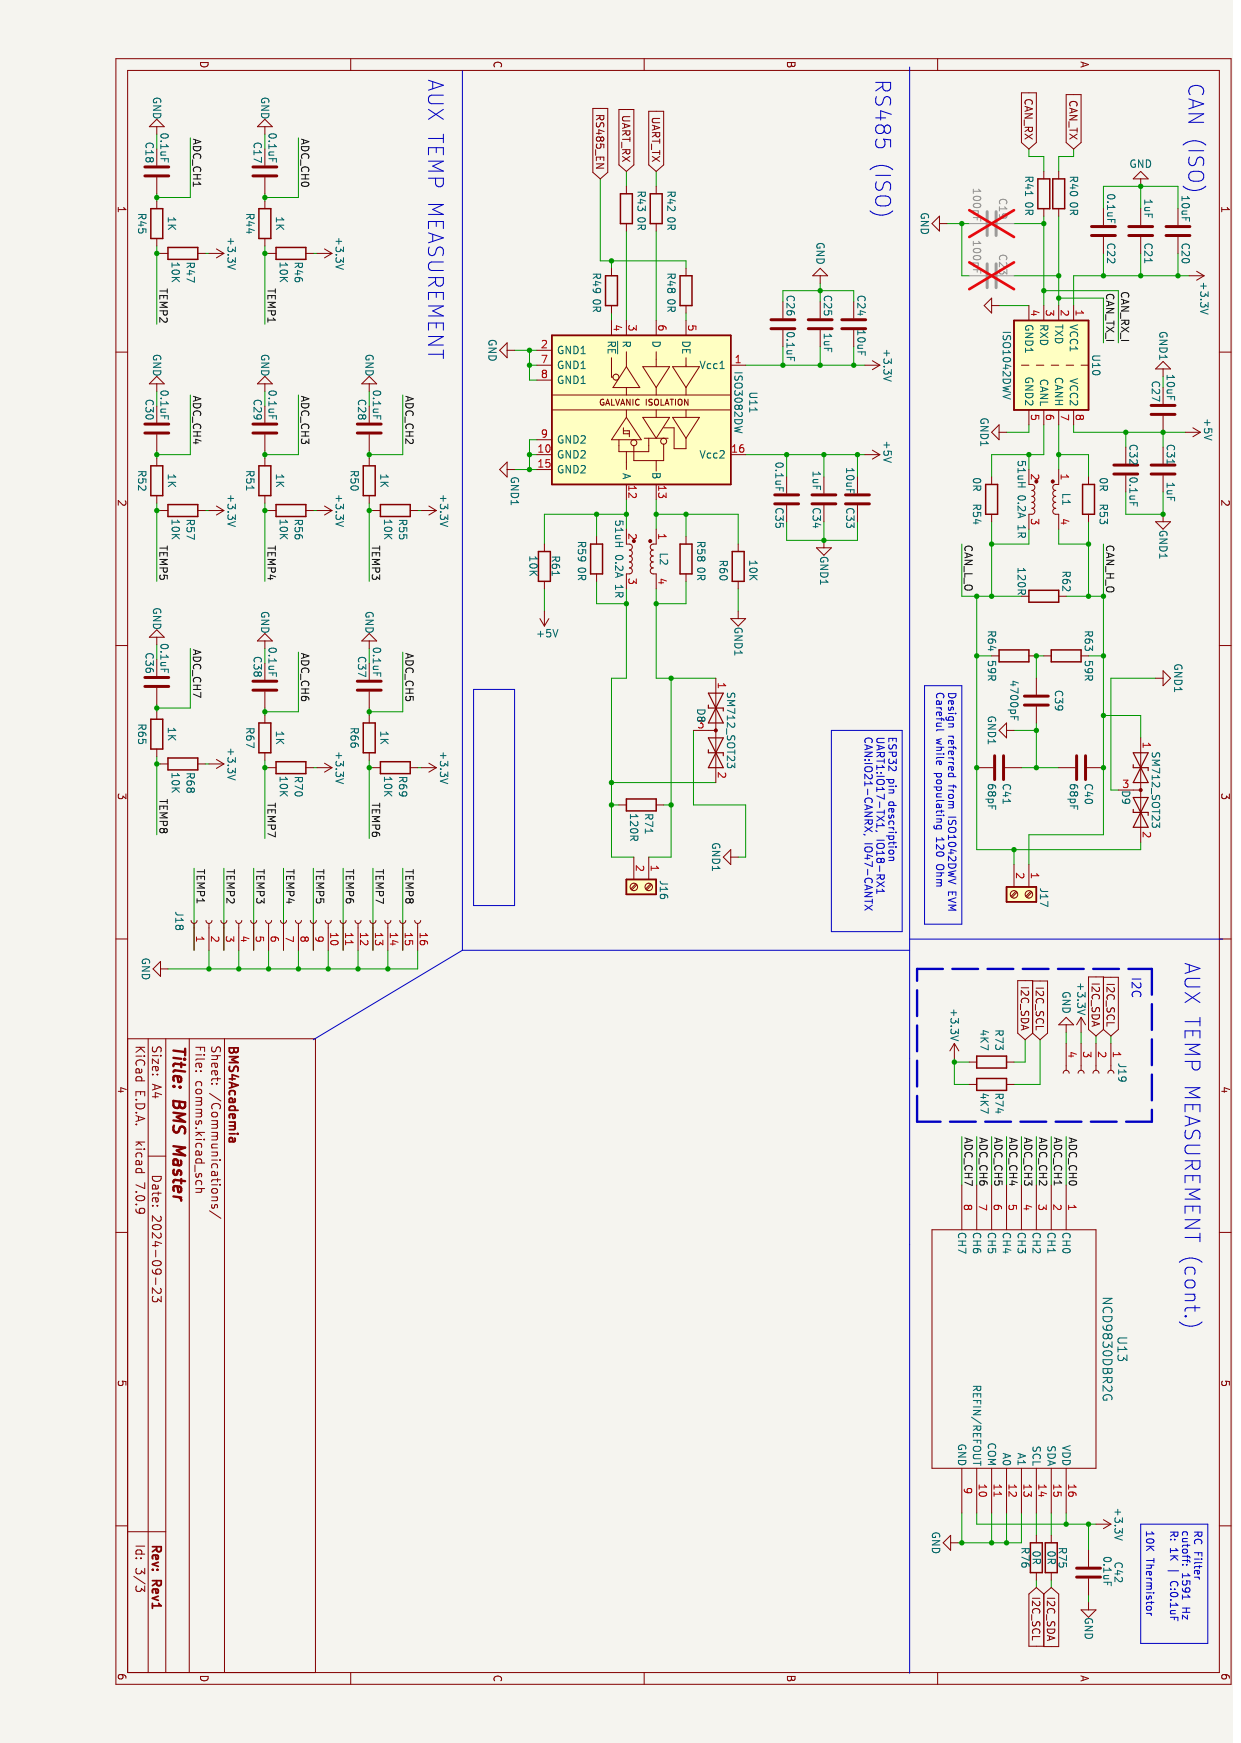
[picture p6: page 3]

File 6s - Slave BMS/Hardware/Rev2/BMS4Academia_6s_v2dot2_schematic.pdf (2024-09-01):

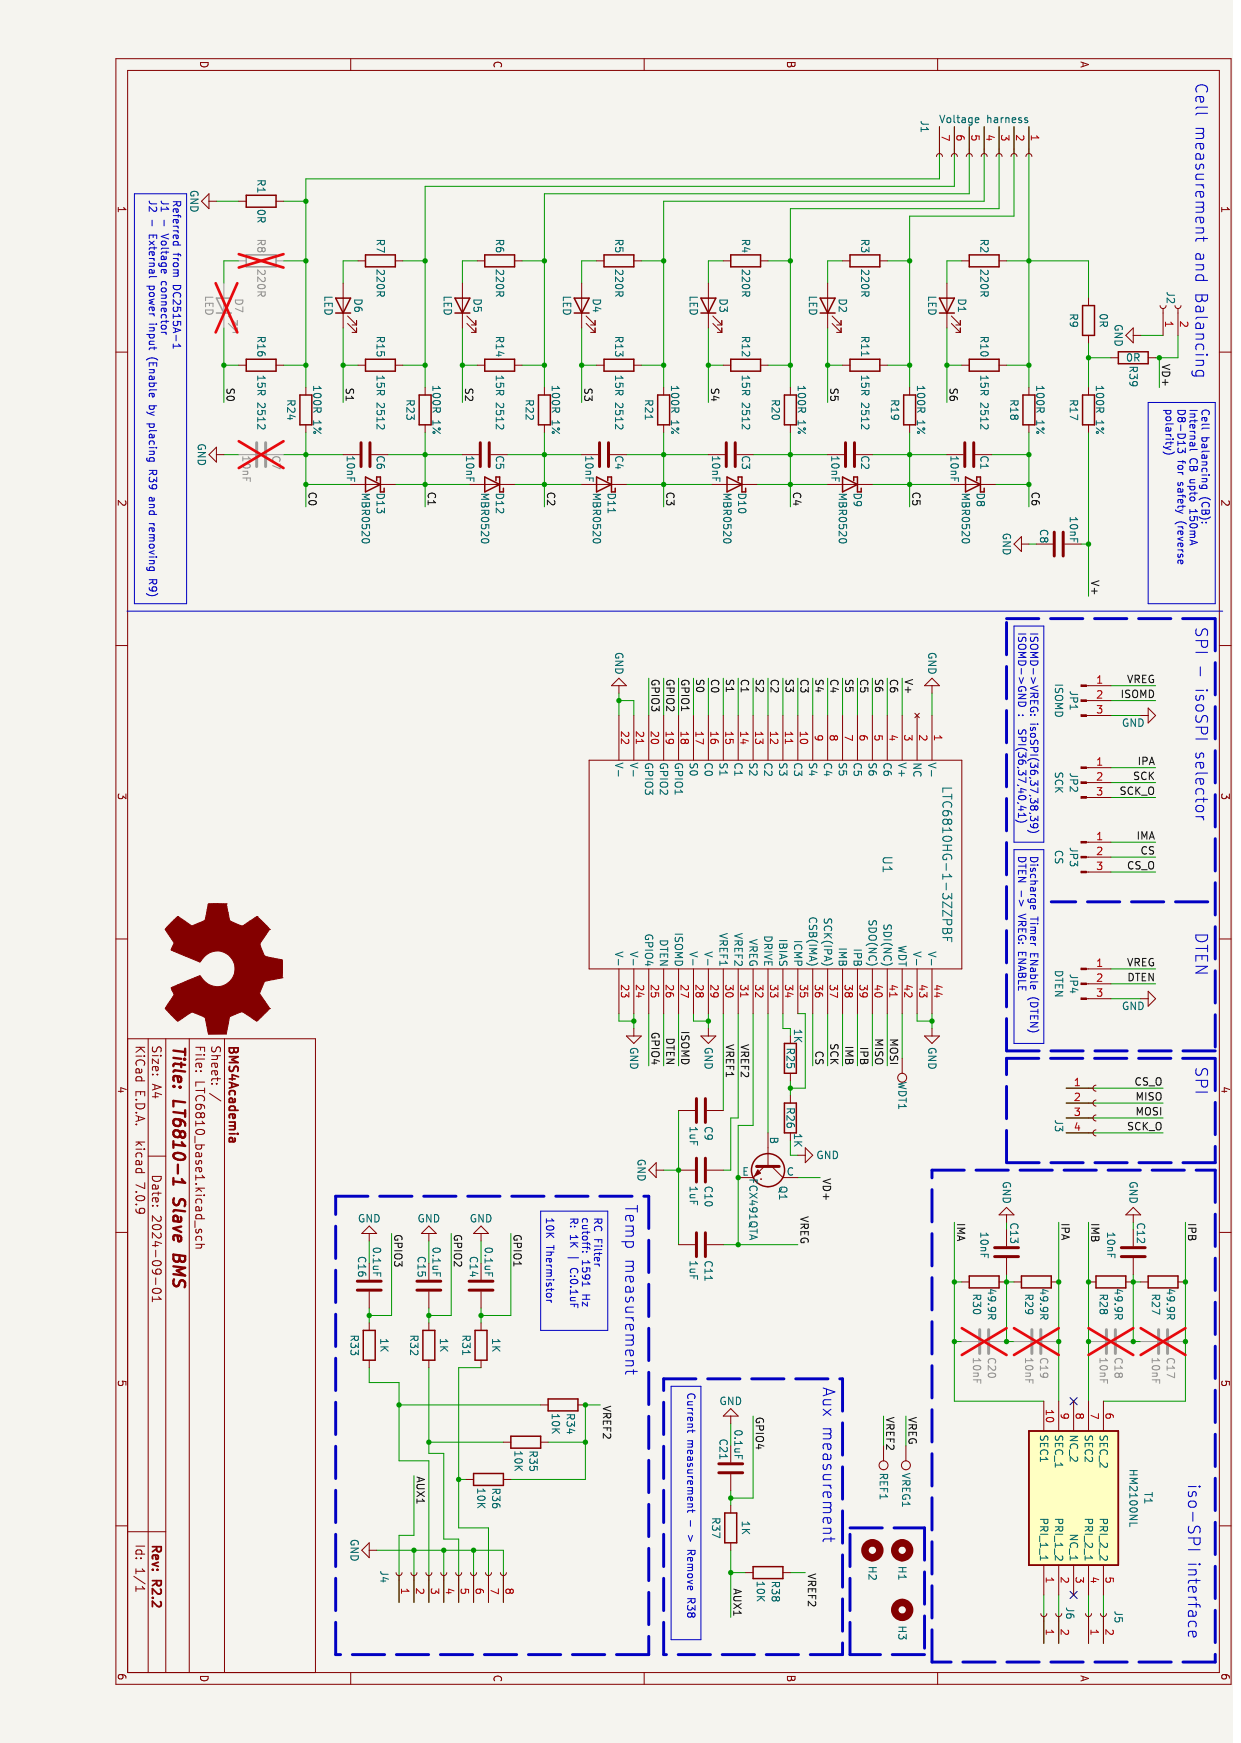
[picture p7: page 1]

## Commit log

2024-09-01 Design files addition v2.2, Stable version
    [BMS4Academia_6s_V2dot2_BOM_01-09-2024.csv, BMS4Academia_6s_v2dot2_CAD.step]
2024-11-17 Design files for 18s BMS rev2 is uploaded.
    [BMS4Academia_18s_LTC6813_rev2_BOM.xlsx]
